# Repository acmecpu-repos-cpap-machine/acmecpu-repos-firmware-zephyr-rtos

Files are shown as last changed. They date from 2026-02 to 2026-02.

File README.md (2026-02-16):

## Zephyr RTOS Setup
To work with this project on **Zephyr RTOS**, follow these steps:

1. **Clone the repository:**
    ```bash
    git clone git@github.com:acmecpu-repos-cpap-machine/acmecpu-repos-firmware-zephyr-rtos.git
    cd acmecpu-repos-firmware-zephyr-rtos
    ```

2. **Install Zephyr and Dependencies:**
    Follow the [Zephyr Getting Started Guide](https://docs.zephyrproject.org/latest/getting_started/index.html) to install Zephyr RTOS and all required dependencies.

3. **Building the Firmware:**
    - Navigate to the desired application folder (e.g., `Blower_Driver_STSPIN32F0A`) and build the project:
    ```bash
    west build -b <your_board> .
    ```

4. **Flashing the Firmware:**
    Flash the firmware to the target hardware using your preferred flashing method (J-Link, ST-Link, etc.).

## CubeIDE Integration
For components that are developed using **STM32CubeIDE**, the IDE project files are located within relevant subfolders. To work with these projects, follow these steps:

1. Open STM32CubeIDE.
2. Import the relevant project (e.g., `Blower_Driver_STSPIN32F0A_E20x`).
3. Build and debug the project as per your requirements.

## Folder Details

### Blower_Driver_STSPIN32F0A
Contains the driver code for controlling the blower motor using **STSPIN32F0A** chip. The code is designed to work with **Zephyr RTOS** to control motor speed, direction, and provide fault monitoring.

### Blower_Driver_STSPIN32F0A_E20x
This folder contains the STM32CubeIDE project for the **STSPIN32F0A** driver, used for platform-specific configuration and debugging.

### altium_device_sheets
Contains the **Altium Designer** files for creating device schematics and PCB designs for Acme CPU hardware. These are used to design various control boards and sensor integration.

### bindings
This folder includes configuration files for various **GPIO** and **sensor** bindings that are required for integrating hardware components with Zephyr.

### bq25611d
Firmware integration for the **BQ25611D** battery management system. The code ensures proper charging, power monitoring, and management of lithium-ion batteries in embedded devices.

### buzzer_generic
This folder contains the driver for controlling a generic buzzer that is used for signaling in embedded applications. It is implemented using Zephyr's device driver framework.

### c201_esp32, c201_stm32g4
These folders contain the firmware for **C201 platform**, one based on **ESP32** and the other on **STM32G4**. These platforms are used for different hardware versions of the control board.

### c202_consolidate
Contains consolidated firmware for the **C202** platform, integrating all the different subsystems into one unified application.

### c20x_algo
This folder includes communication algorithms for the **C20X** series, used in embedded systems for efficient communication and data processing.

### control-board-c201
Contains hardware design files for the **C201 control board**. These are **Altium** files that include the circuit diagrams, PCB layout, and other related documents.

### lib_audio, lib_events, lib_file_oper, etc.
These libraries provide various functionalities such as audio signal processing, event handling, file operations, and more, all implemented for **Zephyr RTOS**. These are generic libraries that can be used across different embedded systems.

## Contributing
If you'd like to contribute to this repository, please follow these guidelines:
1. Fork the repository.
2. Create a new branch for your feature.
3. Make changes and commit them.
4. Submit a pull request to the main branch.
5. For more details please contact feel free to +1 617 401 8929

## License
This project is licensed under the MIT License - see the [LICENSE](LICENSE) file for details.

## Acknowledgements
Special thanks to **Zephyr RTOS** and **CubeIDE** for their continuous support in enabling embedded system development.

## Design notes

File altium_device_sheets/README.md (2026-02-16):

# altium_device_sheets
Repository to maintain Altium Device Sheets

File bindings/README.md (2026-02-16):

# bindings
Zephyr DTS bindings for devices not available on the main Zephyr repository

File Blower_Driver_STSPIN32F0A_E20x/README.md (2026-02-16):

# Blower_Driver_STSPIN32F0A_E20x
STSPIN32F0A based motor driver used in e20x series boards

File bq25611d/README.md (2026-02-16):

# bq25611d
Zephyr device driver for TI battery charger BQ25611D

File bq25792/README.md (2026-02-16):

# bq25792
Zephyr device driver for BQ25792 battery charger

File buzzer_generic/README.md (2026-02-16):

# buzzer_generic
Zephyr device driver for a generic buzzer

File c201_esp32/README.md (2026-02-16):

# C201 ESP32 Firmware

Repository to contain source files for the ESP32 based firmware for Control Board Model C201

## CLI commands to build, flash and monitor

- First export the environment by
`. $HOME/esp/esp-idf/export.sh`

- to build run
`idf.py build`

- to flash and monitor run (check your USB number by `ls -l /dev/ttyUSB*`)
`idf.py -p /dev/ttyUSB0 flash monitor`

- to erase the flash memory run
`idf.py -p /dev/ttyUSB0 erase_flash`

## Use Eclipse IDE to build, flash, monitor and debug

[GitHub - espressif/idf-eclipse-plugin: Eclipse plugin for ESP-IDF CMake based projects (4.x and above)](https://github.com/espressif/idf-eclipse-plugin#installing-idf-plugin-using-update-site-url)

[Using Debugger - ESP32 - — ESP-IDF Programming Guide v4.2 documentation](https://docs.espressif.com/projects/esp-idf/en/stable/esp32/api-guides/jtag-debugging/using-debugger.html#jtag-debugging-using-debugger-eclipse)

[JTAG Debugging - ESP32 - — ESP-IDF Programming Guide v4.2 documentation](https://docs.espressif.com/projects/esp-idf/en/stable/esp32/api-guides/jtag-debugging/index.html)

[esp-iot-solution/ESP-Prog_guide_en.md at master · espressif/esp-iot-solution](https://github.com/espressif/esp-iot-solution/blob/master/documents/evaluation_boards/ESP-Prog_guide_en.md)

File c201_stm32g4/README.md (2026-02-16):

# c201_stm32g4

Repository to contain source files for the STM32G473 based firmware for Control Board Model C201

# Build the project

Assuming the path to the project is $HOME/git/acme_cpu/c201_stm32g4/ and $HOME/zephyrproject/zephyr is the path to the Zephyr source code:

cd $HOME/zephyrproject/zephyr

source zephyr-env.sh (one time action to configure environment variables)

west build -p always -d $HOME/git/acme_cpu/c201_stm32g4/build $HOME/git/acme_cpu/c201_stm32g4/source -G"Eclipse CDT4 - Ninja"

or

west build -p auto -d $HOME/git/acme_cpu/c201_stm32g4/build $HOME/git/acme_cpu/c201_stm32g4/source -G"Eclipse CDT4 - Ninja"

if you do not necessarily need to build the project in a "pristine" build directory.

# Open the project in Eclipse IDE

Menu -> File -> Open Projects from File System...-> Select $HOME/git/acme_cpu/c201_stm32g4/ folder -> Open -> Select c201_stm32g4/build -> Finish

# Launch a GUI-based configuration tool (Kconfig)

cd $HOME/zephyrproject/zephyr

source zephyr-env.sh (one time action to configure environment variables)

west build -d $HOME/git/acme_cpu/c201_stm32g4/build -t guiconfig

# Flash a MCU with west

cd $HOME/zephyrproject/zephyr

source zephyr-env.sh (one time action to configure environment variables)

west flash -d $HOME/git/acme_cpu/c201_stm32g4/build --board-dir $HOME/git/acme_cpu/c201_stm32g4/source/boards\
	 -r openocd --config $HOME/git/acme_cpu/c201_stm32g4/source/boards/arm/stm32g473_acme_cpu_c201/support/openocd_st-link.cfg

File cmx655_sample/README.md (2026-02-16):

# cmx655_sample
Audio record and playback sample code using CMX655D audio codec

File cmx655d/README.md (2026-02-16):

# cmx655d
Zephyr device driver for CM655D Audio Codec

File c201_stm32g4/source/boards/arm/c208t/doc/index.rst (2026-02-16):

C208t board
################

Overview
********

Hardware
********

Supported Features
==================

System Clock
------------

Serial Port
-----------

Programming and Debugging
*************************

Flashing
========

Debugging
=========

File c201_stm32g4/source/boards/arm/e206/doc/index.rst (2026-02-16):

E206 board
################

Overview
********

Hardware
********

Supported Features
==================

System Clock
------------

Serial Port
-----------

Programming and Debugging
*************************

Flashing
========

Debugging
=========

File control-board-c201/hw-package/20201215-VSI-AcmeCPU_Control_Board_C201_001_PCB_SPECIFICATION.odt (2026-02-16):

Specification for PCB: Control_Board_C201.PcbDoc

The 6-layer PCB is intended for manual and automatic soldering of SMT and THT parts on the top and bottom sides .

General requirements

IPC-A-600/6010 class 2

Laminate

Laminate: IPC 4101/21 with minimum Tg=130°C

Flammability: V0 according to UL94

CTI index 3: 175 < CTI ≤ 400 or better

CTE: Pre-Tg. 60ppm/°C Post-Tg. 300ppm/°C

Copper plating

Hole plating: min. 20μm. and min. avg. 25μm according to IPC-6012 class 3

Dimensions and Marking

PCB Size (X,Y): 100x70 mm

Tolerances on outline dimensions: +/- 0.2mm

Layer stackup

The PCB stack is in the picture below. The total thickness of the PCB is 1,22 mm ±10%.

Controlled impedance traces

Controlled impedance traces are as follows.

Layer | Impedance Structure | Trace width, mm | Diff line space, mm | 1 ref. plane | 2 ref. plane | Target Impedance, Ohm*
1 | Edge Coupled Coated Microstrip | 0.152 | 0.152 | 2 | - | 90 diff
1 | Single Ended | 0.152 | - | 2 | - | 50
2
3
4
5
6

*Tolerance on all impedances is ±10%.

Solder mask

Liquid film or electrostatic spray coating on top and bottom sides .

According to: IPC-SM-840E, Class T

Minimum thickness: 8μm

Maximum thickness: 30μm

Legend:

Silkscreen Colour: White on top and bottom layers.

Plugged via holes:

Via holes covered by solder mask on both sides must be plugged.

Via holes with solder mask opening on one side and covered by solder mask on the other side, must be plugged from the same side they are covered by solder mask – solder mask opening on the other side must remain.

Surface finish

ENIG – Au 0.05 μm / Ni 3.0 μm;

Solderability accordingly to IPC J-STD-003, test C1 PTH, SMD test F1 set A

Gerber data (.\Manufacturing\Gerber Files)

Filename | Contents
20201215-VSI-AcmeCPU_Control_Board_C201_001_PCB_SPECIFICATION.pdf | This file
20201215-VSI-Acme_CPU_Control_Board_C201_001_Gerber.GTL | Layer 1, 1-SIG-Top
20201215-VSI-Acme_CPU_Control_Board_C201_001_Gerber.GP1 | Layer 2, 2-GND
20201215-VSI-Acme_CPU_Control_Board_C201_001_Gerber.GP2 | Layer 3, 3-PWR
20201215-VSI-Acme_CPU_Control_Board_C201_001_Gerber.G1 | Layer 4, 4-SIG-HOR
20201215-VSI-Acme_CPU_Control_Board_C201_001_Gerber.G2 | Layer 5, 5-SIG-VERT
20201215-VSI-Acme_CPU_Control_Board_C201_001_Gerber.GBL | Layer 6, 6-GND-BOT
20201215-VSI-Acme_CPU_Control_Board_C201_001_Gerber.GTO | Top Overlay (Top Silk)
20201215-VSI-Acme_CPU_Control_Board_C201_001_Gerber.GTS | Top Solder (Solder Mask)
20201215-VSI-Acme_CPU_Control_Board_C201_001_Gerber.GBS | Bottom Solder (Solder Mask)
20201215-VSI-Acme_CPU_Control_Board_C201_001_Gerber.GBO | Bottom Overlay
20201215-VSI-Acme_CPU_Control_Board_C201_001_Gerber.GM12 | Board Outline
20201215-VSI-Acme_CPU_Control_Board_C201_001_Gerber.GD1 | Drill Drawing
20201215-VSI-Acme_CPU_Control_Board_C201_001_Gerber.GG1 | Drill Guide
20201215-VSI-Acme_CPU_Control_Board_C201_001_Gerber.GM14 | Top Assembly
20201215-VSI-Acme_CPU_Control_Board_C201_001_Gerber.GM19 | Bottom Assembly

Stencils (.\Manufacturing\Stencil Files)

Filename | Contents
20201215-VSI-Acme_CPU_Control_Board_C201_001_Stencil.GTP | Top Paste
20201215-VSI-Acme_CPU_Control_Board_C201_001_Stencil.GBP | Bottom Paste

Drill and milling data (.\Manufacturing\Gerber Files)

Filename | Contents
20201215-VSI-Acme_CPU_Control_Board_C201_001_NC_Drill-RoundHoles-NonPlated.TXT | NCDrill Non-plated Round Holes File
20201215-VSI-Acme_CPU_Control_Board_C201_001_NC_Drill-SlotHoles-Plated.TXT | NCDrill Plated Slot Holes File
20201215-VSI-30041113_Acme_CPU_Control_Board_C201_001_NC_Drill-RoundHoles-Plated.TXT | NCDrill Plated Round Holes File

Text Reports

Filename | Contents
20201215-VSI-Acme_CPU_Control_Board_C201_001_Gerber.REP | Gerber Generation report
20201215-VSI-Acme_CPU_Control_Board_C201_001_Gerber.EXTREP | Gerber File Extension Report
20201215-VSI-Acme_CPU_Control_Board_C201_001_NC_Drill.DRR | NCDrill File Report
20201215-VSI-Acme_CPU_Control_Board_C201_001_Stencil.REP | Stencil Generation report
20201215-VSI-Acme_CPU_Control_Board_C201_001_Stencil.EXTREP | Gerber File Extension Report

Schematic (.\Design\Schematic - pdf)

Assembly Drawings (.\Assembly\PCB Layout - pdf)

20201215-VSI-Acme_CPU_Control_Board_C201_001_PCB.PDF

20201215-VSI-Acme_CPU_Control_Board_C201_001_DWG.PDF

Pick and Place (.\Assembly\Pick_n_Place)

BG95-M3_Global_TFT_SCREEN\20201215-VSI-Acme_CPU_Control_Board_C201_001_Pick_and_Place.txt

BOM (.\Assembly\BOM - Excel)

BG95-M3_Global_TFT_SCREEN\20201215-VSI-Acme_CPU_Control_Board_C201_001_BG95-M3_Global_TFT_SCREEN_DFM_BOM.xls

Additional info

Mechanical Files (.\Assembly\Mechanical)

No Variations\20201215-VSI-Acme_CPU_Control_Board_C201_001_DXF_Model.DXF

BG95-M3_Global_TFT_SCREEN\20201215-VSI-Acme_CPU_Control_Board_C201_001_BG95-M3_Global_TFT_SCREEN_3D.step

General

Extended gerber / excellon drill.

Layout

Filename: Altium 17.1: Control_Board_Model_C201_FFC_Sens_Conn.PcbDoc

Fiducials

TOP FID1: 2.54mm; 62.865mm

TOP FID2: 2.54mm; 7.62mm

TOP FID3: 93.98mm; 6.35mm

BOT FID1: 2.54mm; 62.865mm

BOT FID2: 2.54mm; 7.62mm

BOT FID3: 93.98mm; 6.35mm

Contacts

If there are any questions regarding the layout please contact:

HW Developer

Volodymyr Sirous

Email: volodymyr@acmecpu.com

Project Manager

Pankaj Gupta

Email: pg@acmecpu.com

Homepage: www.acmecpu.com

Acme CPU PCB Specification Page 2/4 Date: 20201215 Acme_CPU_Control_Board_C201_001 Responsible: VSI

Acme CPU 30 N Gould St suite 4000 ● Sheridan WY 82801 ● USA (http://www.ektos.net/)● (http://www.ektos.net/)info@acmecpu.com (http://www.ektos.net/)● (http://www.ektos.net/)http://www.acmecpu.com

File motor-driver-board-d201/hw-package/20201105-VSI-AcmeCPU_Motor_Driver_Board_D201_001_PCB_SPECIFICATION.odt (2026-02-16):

Specification for PCB: Motor_Driver_D201.PcbDoc

The 4-layer PCB is intended for manual and automatic soldering of SMT and THT parts on the top side.

General requirements

IPC-A-600/6010 class 2

Laminate

Laminate: IPC 4101/124 with minimum Tg=150°C

Flammability: V0 according to UL94

CTI index 3: 175 < CTI ≤ 400 or better

CTE: Pre-Tg. 60ppm/°C Post-Tg. 300ppm/°C

Copper plating

Hole plating: min. 20μm. and min. avg. 25μm according to IPC-6012 class 3

Dimensions and Marking

PCB Size (X,Y): 20x30 mm

Tolerances on outline dimensions: +/- 0.2mm

Layer stackup

The PCB stack is in the picture below. The total thickness of the PCB is 0,98 mm ±10%.

Controlled impedance traces

There is no need to control impedance of traces on the PCB.

Layer | Impedance Structure | Trace width, mm | Diff line space, mm | 1 ref. plane | 2 ref. plane | Target Impedance, Ohm*
1
2
3
4
5
6

*Tolerance on all impedances is ±10%.

Solder mask

Liquid film or electrostatic spray coating on top and bottom sides .

According to: IPC-SM-840E, Class T

Minimum thickness: 8μm

Maximum thickness: 30μm

Legend:

Silkscreen Colour: White on top and bottom layers.

Plugged via holes:

Via holes covered by solder mask on both sides must be plugged.

Via holes with solder mask opening on one side and covered by solder mask on the other side, must be plugged from the same side they are covered by solder mask – solder mask opening on the other side must remain.

Surface finish

ENIG – Au 0.05 μm / Ni 3.0 μm;

Solderability accordingly to IPC J-STD-003, test C1 PTH, SMD test F1 set A

Gerber data (.\Manufacturing\Gerber Files)

Filename | Contents
20201105-VSI-AcmeCPU_Motor_Driver_Board_D201_001_PCB_SPECIFICATION.pdf | This file
20201105-VSI-Acme_CPU_Motor_Driver_D201_001_Gerber.GTL | Layer 1, 1-SIG-Top
20201105-VSI-Acme_CPU_Motor_Driver_D201_001_Gerber.GP1 | Layer 2, 2-GND
20201105-VSI-Acme_CPU_Motor_Driver_D201_001_Gerber.GP2 | Layer 3, 3-GND-PWR
20201105-VSI-Acme_CPU_Motor_Driver_D201_001_Gerber.GBL | Layer 4, 4-SIG-BOT
20201105-VSI-Acme_CPU_Motor_Driver_D201_001_Gerber.GTO | Top Overlay (Top Silk)
20201105-VSI-Acme_CPU_Motor_Driver_D201_001_Gerber.GTS | Top Solder (Solder Mask)
20201105-VSI-Acme_CPU_Motor_Driver_D201_001_Gerber.GBS | Bottom Solder (Solder Mask)
20201105-VSI-Acme_CPU_Motor_Driver_D201_001_Gerber.GBO | Bottom Overlay
20201105-VSI-Acme_CPU_Motor_Driver_D201_001_Gerber.GM12 | Board Outline
20201105-VSI-Acme_CPU_Motor_Driver_D201_001_Gerber.GD1 | Drill Drawing
20201105-VSI-Acme_CPU_Motor_Driver_D201_001_Gerber.GG1 | Drill Guide
20201105-VSI-Acme_CPU_Motor_Driver_D201_001_Gerber.GM14 | Top Assembly

Stencils (.\Manufacturing\Stencil Files)

Filename | Contents
20201105-VSI-Acme_CPU_Motor_Driver_D201_001_Stencil.GTP | Top Paste

Drill and milling data (.\Manufacturing\Gerber Files)

Filename | Contents
20201105-VSI-30041113_Acme_CPU_Motor_Driver_D201_001_NC_Drill-Plated.TXT | NCDrill Plated Holes File

Text Reports

Filename | Contents
20201105-VSI-Acme_CPU_Motor_Driver_D201_001_Gerber.REP | Gerber Generation report
20201105-VSI-Acme_CPU_Motor_Driver_D201_001_Gerber.EXTREP | Gerber File Extension Report
20201105-VSI-Acme_CPU_Motor_Driver_D201_001_NC_Drill.DRR | NCDrill File Report
20201105-VSI-Acme_CPU_Motor_Driver_D201_001_Stencil.REP | Stencil Generation report
20201105-VSI-Acme_CPU_Motor_Driver_D201_001_Stencil.EXTREP | Gerber File Extension Report

Schematic (.\Design\Schematic - pdf)

20201105-VSI-Acme_CPU_Motor_Driver_D201_001_No Variations.PDF

Assembly Drawings (.\Assembly\PCB Layout - pdf)

20201105-VSI-Acme_CPU_Motor_Driver_D201_001_PCB.PDF

Pick and Place (.\Assembly\Pick_n_Place)

20201105-VSI-Acme_CPU_Motor_Driver_D201_001_Pick_and_Place.txt

BOM (.\Assembly\BOM - Excel)

20201105-VSI-Acme_CPU_Motor_Driver_D201_001_No_Variatoins_DFM_BOM.xls

Additional info

Mechanical Files (.\Assembly\Mechanical)

20201105-VSI-Acme_CPU_Motor_Driver_D201_001_Plain_AutoCAD.DXF

20201105-VSI-Acme_CPU_Motor_Driver_D201_001_3D_STEP.step

General

Extended gerber / excellon drill.

Layout

Filename: Altium 17.1: Motor_Driver_D201.PcbDoc

Fiducials

TOP FID1: 7.50mm; 18.00mm

TOP FID2: 20.50mm; 18.00mm

TOP FID3: 27.94mm; 7.62mm

Contacts

If there are any questions regarding the layout please contact:

HW Developer

Volodymyr Sirous

Email: volodymyr@acmecpu.com

Project Manager

Pankaj Gupta

Email: pg@acmecpu.com

Homepage: www.acmecpu.com

Acme CPU PCB Specification Page 2/4 Date: 20201105 Acme_CPU_Motor_Driver_D201_001 Responsible: VSI

Acme CPU 30 N Gould St suite 4000 ● Sheridan WY 82801 ● USA (http://www.ektos.net/)● (http://www.ektos.net/)info@acmecpu.com (http://www.ektos.net/)● (http://www.ektos.net/)http://www.acmecpu.com

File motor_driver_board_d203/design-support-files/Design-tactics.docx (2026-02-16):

1. Separated Microcontroller Portion from High Power circuitry.

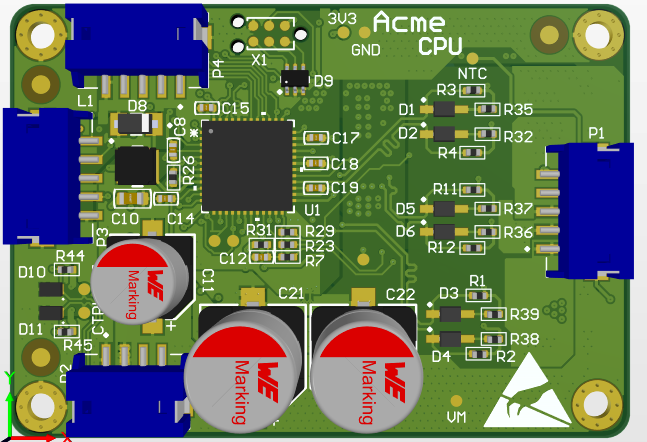
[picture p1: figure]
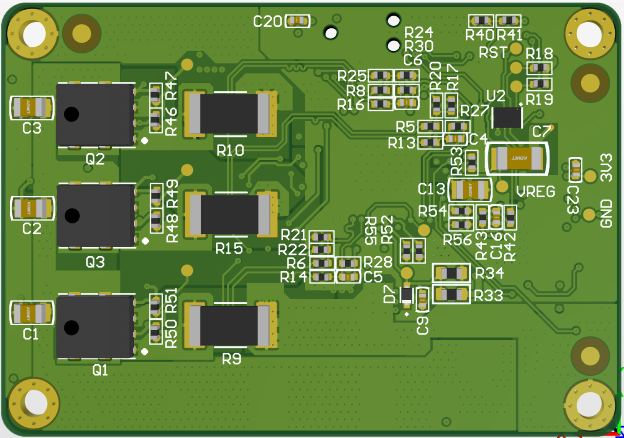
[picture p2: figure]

2. Placed the Input Connector as close as possible to compensate with the shorter high power path to the H-Bridge Section.
3. Minimized the AC loop Area. Used Multilayer return topology to return the Current. Since the Internal Plane layers does not have air proximity, multilayer return path is useful to reduce the resistance (Lowering the heat dissipation due to high current flow).

POWER SOURCE LAYERs

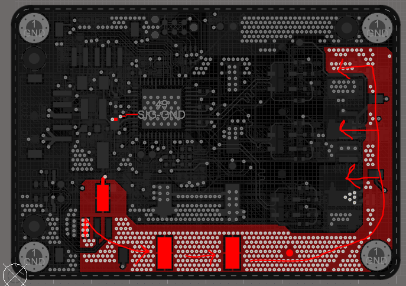
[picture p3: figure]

The Motor Power flowing through the 1st Layer (TOP)

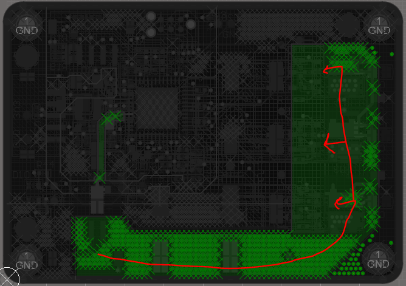
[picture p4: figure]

The Motor Power flowing through the 2md Layer

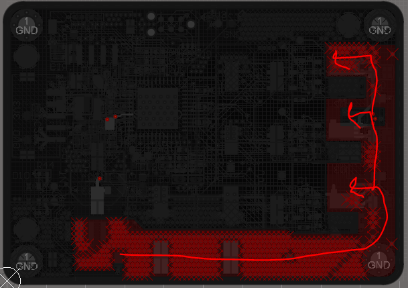
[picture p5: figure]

The Motor Power flowing through the 3rd Layer

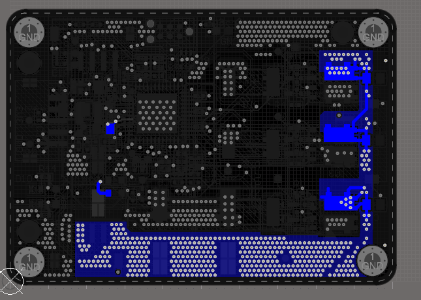
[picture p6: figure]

The Motor Power flowing through the 4^t^h Layer (BOTTOM)

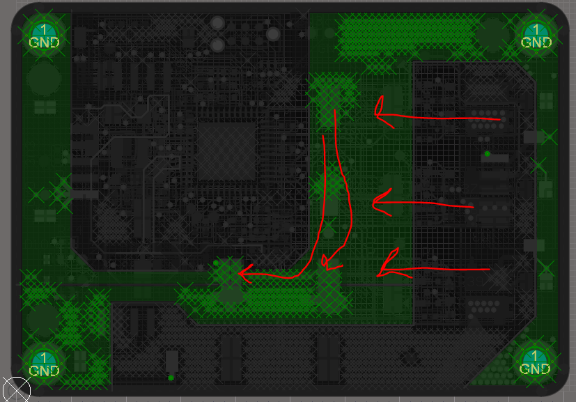
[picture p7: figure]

GROUND REURN LAYERs

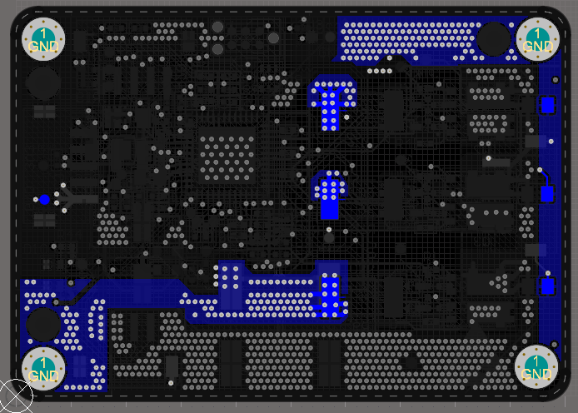
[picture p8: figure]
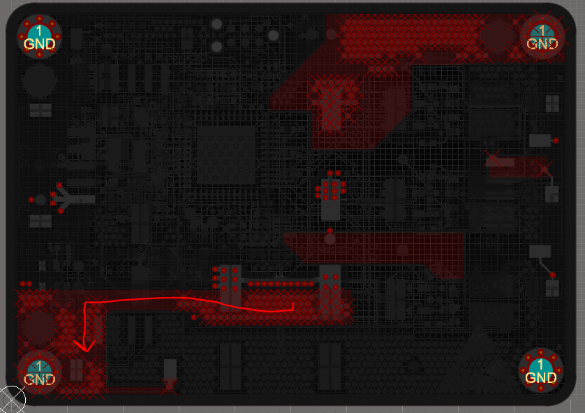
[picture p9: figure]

The Motor Current Returning to the Input Filter Caps.

The current is coming to the Input Power port through the
Capacitor using the 3rd Layer.

The current is also coming to the Input Power port through
the Capacitor using the 4th Layer.

4. Separation of Ground Paths and isolation are done to reduce unwanted noise injunction. Returned to the Bulk Capacitor. As two Bulk capacitors are used to reduce increase the capacitance, decreasing the height and lowering the ESR value, the separation of ground on start pattern is done.

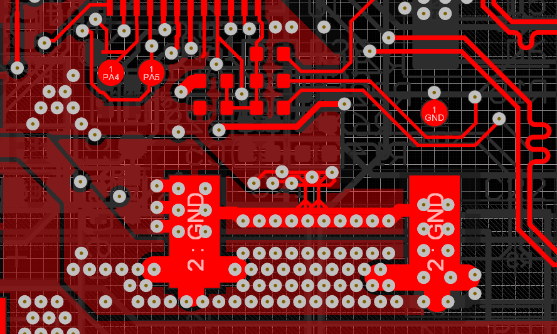
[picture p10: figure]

Two net ties are used to separate the MCU Ground from the Power Ground and joined across in between of the Bulk Caps Pads.

Different Ground Signal Return Paths (Primary Layer shown only)–

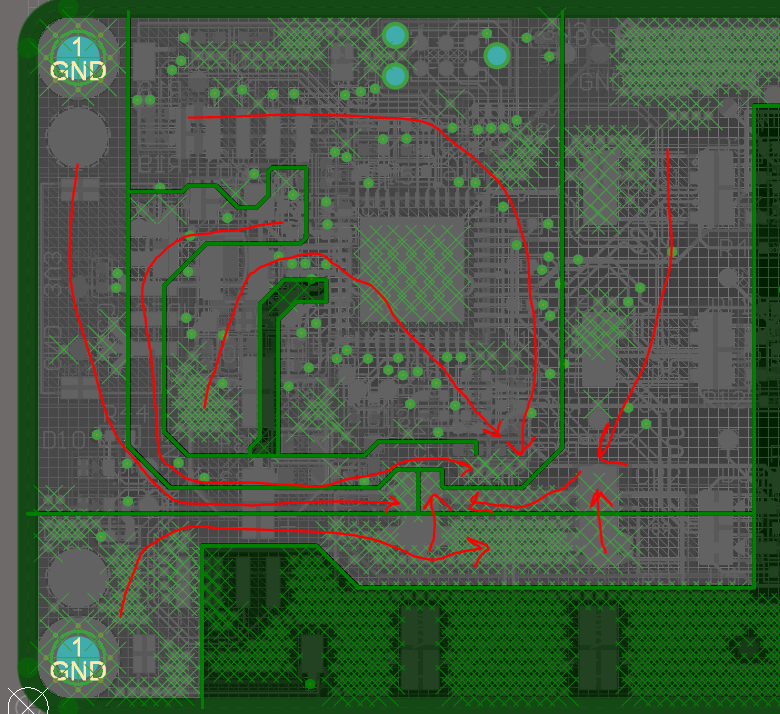
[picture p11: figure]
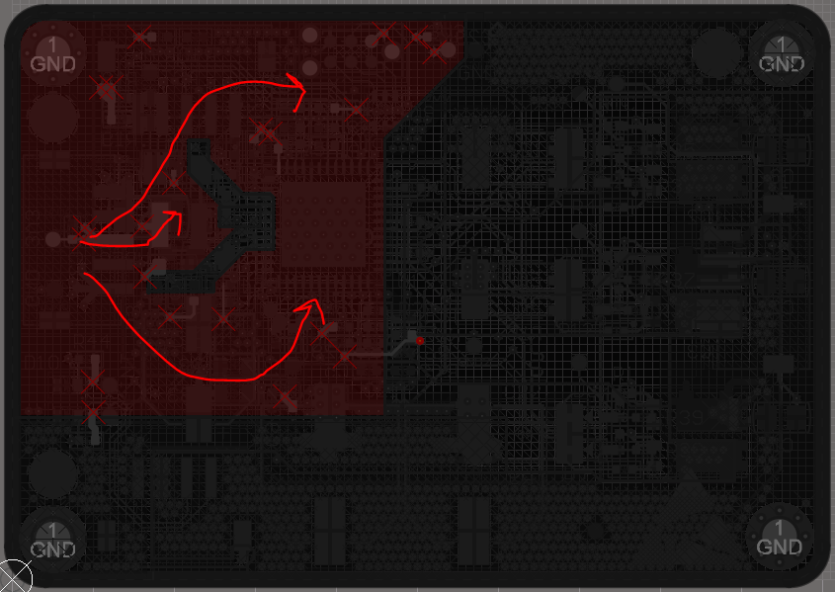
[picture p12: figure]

5. Separate MCU Power Path Created for 3.3V line which comes from external regulator sources out of the board. Close proximity of the Filter capacitors are placed.

The return path goes like this –

MCU Ground & sense circuit ground-> Bulk Capacitor -> Input Connector.

[Please note: The ground for the Motor Power and 3.3V external Ground are connected to the same source coming from external Power circuit]

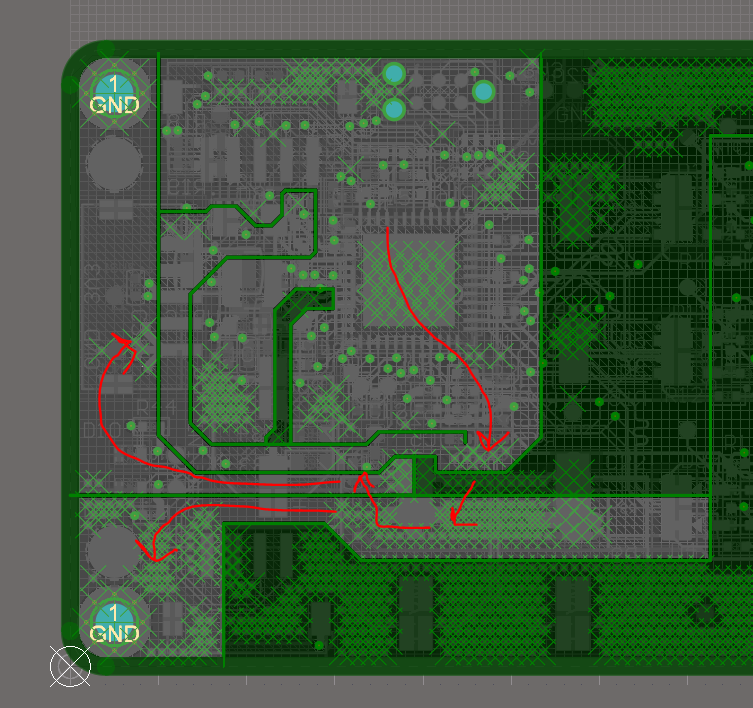
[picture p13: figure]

6. Array of Vias and Multi-layer Planes are used to carry current.
7. Gate resistor and circuitry are placed into close proximity.

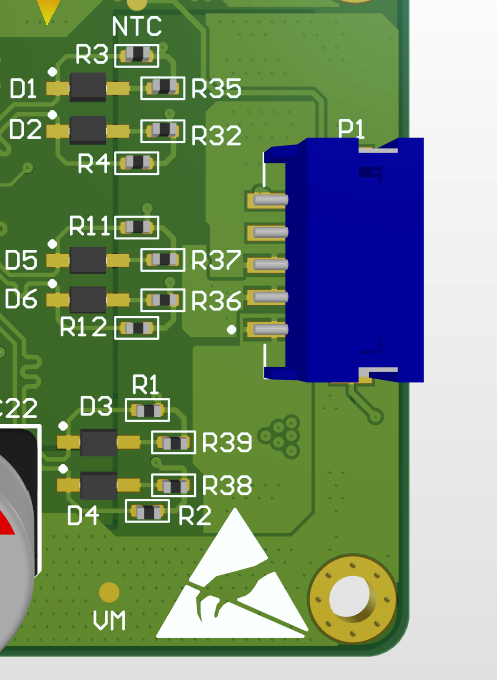
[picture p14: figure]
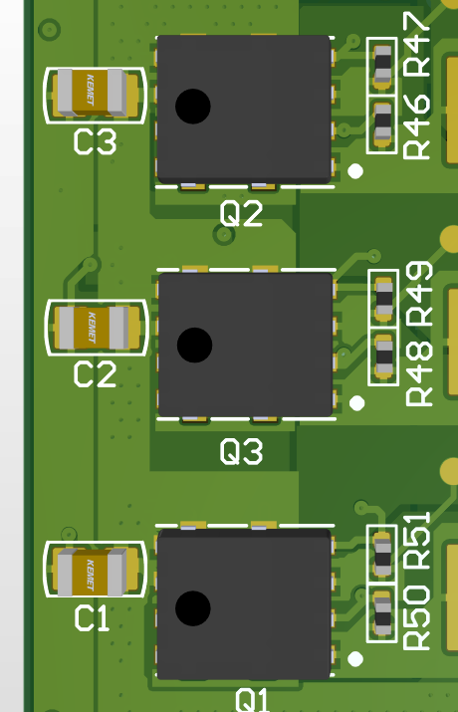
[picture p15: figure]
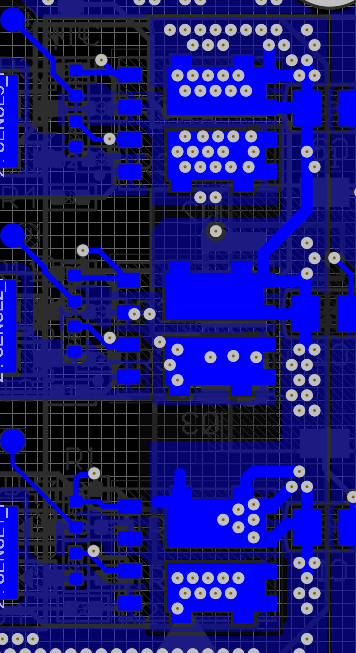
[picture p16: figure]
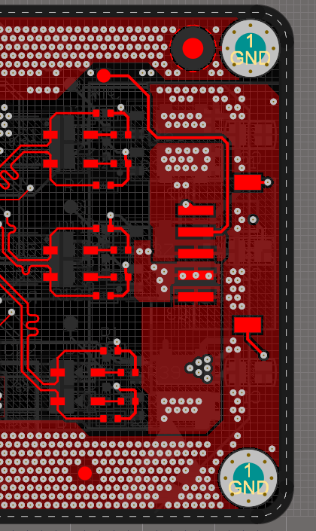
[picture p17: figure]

8. Kelvin sensing used and differential length tuning is done.

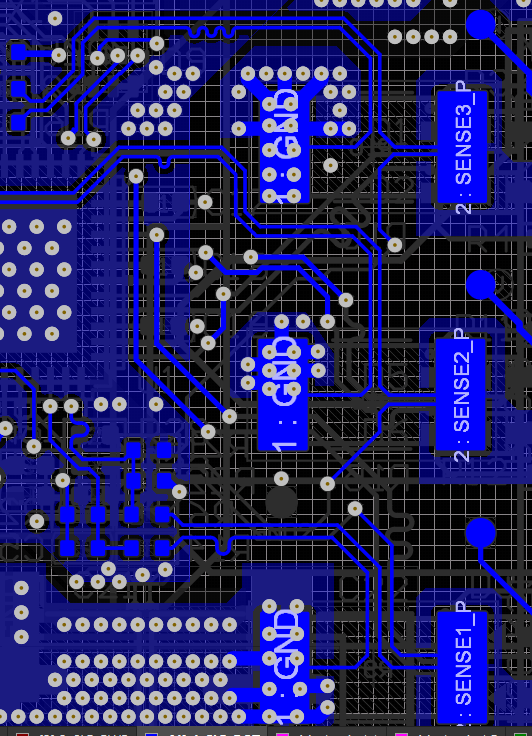
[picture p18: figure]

Op-Amp differential inputs are also tuned –

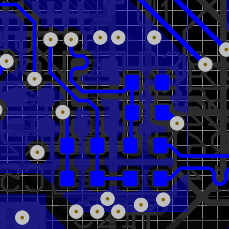
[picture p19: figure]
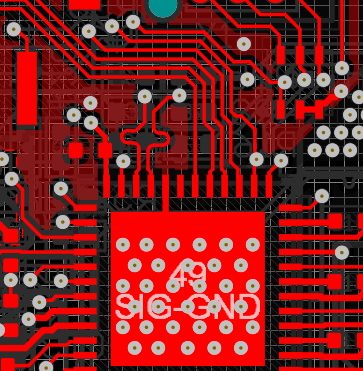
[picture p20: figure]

9. Gate driver of Three phases – Low Side and High Sides are connected parallel, differential pairs used where length tuning is done.

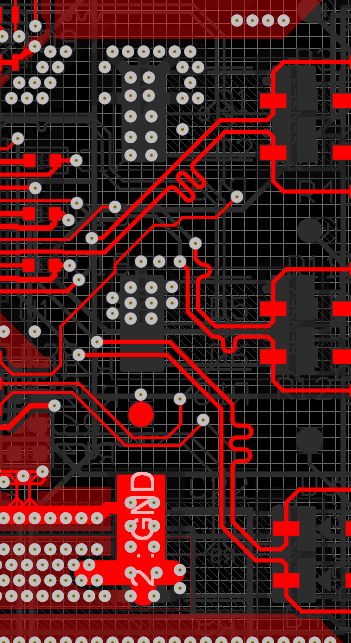
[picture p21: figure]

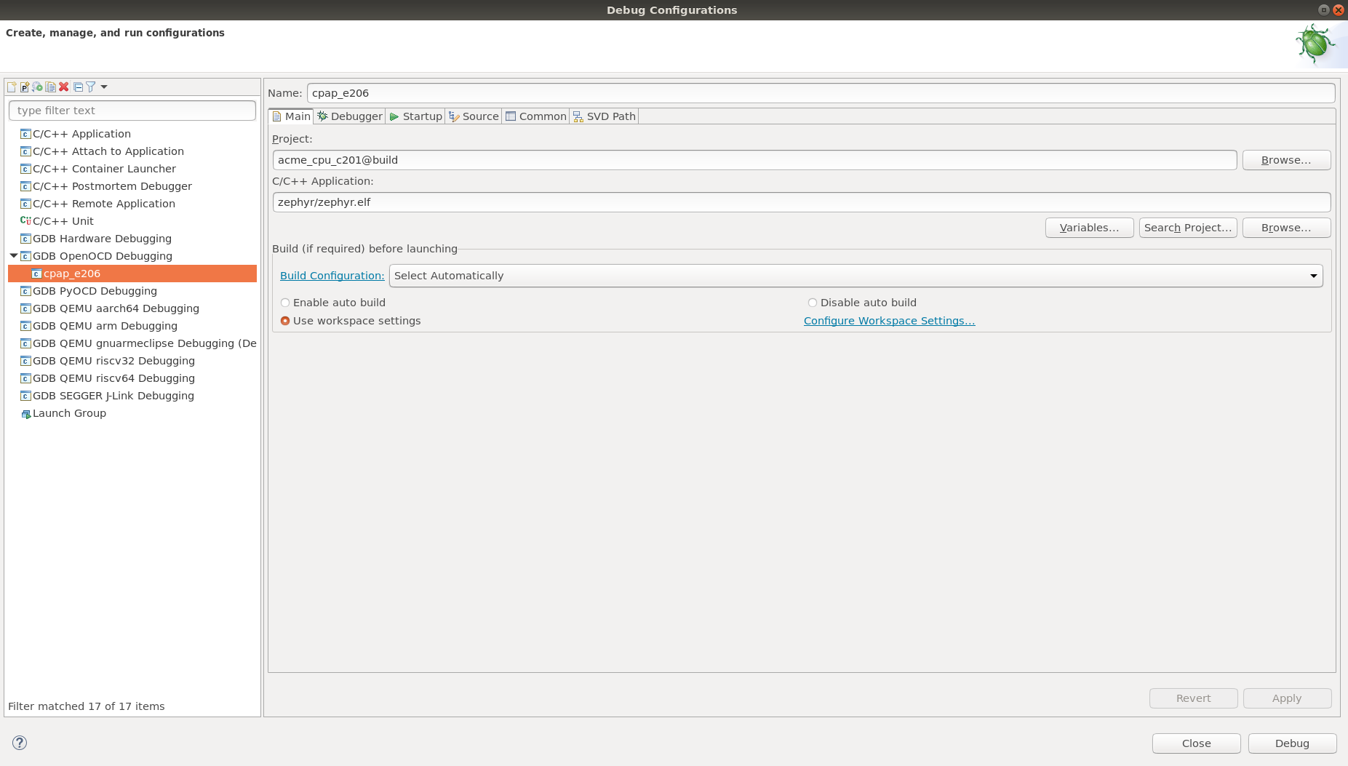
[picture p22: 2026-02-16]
firmware_general/openocd/openocd_eclipse_main.png

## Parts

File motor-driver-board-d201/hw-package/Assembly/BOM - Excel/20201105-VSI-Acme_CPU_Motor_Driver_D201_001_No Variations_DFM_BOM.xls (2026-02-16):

Designator | Quantity | Manufacturer | Manufacturer Part Number | Comment | Description | Footprint | Mount | Layer | Supplier 1 | Supplier Part Number 1
C1, C4, C9, C10 | 4.0 | TDK | CGA2B3X7R1H104K050BB | CAP CER 0.1UF 50V X7R 0402, CAP CER 0.1UF 50V X7R 0402, CGA2B3X7R1H104K050BB, CGA2B3X7R1H104K050BB | 0.1µF ±10% 50V Ceramic Capacitor X7R 0402 (1005 Metric) | C0402 | Surface Mount | Top | Digi-Key | 445-6899-1-ND
C2, C3, C8 | 3.0 | Yageo | CC0402KRX5R5BB105 | CAP CER 1UF 6.3V X5R 0402 | 1µF ±10% 6.3V Ceramic Capacitor X5R 0402 (1005 Metric) | C0402 | Surface Mount | Top | Digi-Key | 311-1438-1-ND
C5 | 1.0 | Yageo | CC0805MKX5R8BB226 | CAP CER 22UF 25V X5R 0805 | 22µF ±20% 25V Ceramic Capacitor X5R 0805 (2012 Metric) | C0805 | Surface Mount | Top | Digi-Key | 311-1903-1-ND
C6 | 1.0 | Murata | GRM21BR71A106KA73L | CAP CER 10uF X7R 10% 0805 | Capacitor,10uF,10V,X7R,10%,0805,Murata | C0805 | Surface Mount | Top | Digi-Key | 490-10516-1-ND
C7 | 1.0 | Wurth Elektronik | 865080443009 | CAP ALUM 68 UF 20% 25 V SMD | WCAP-ASLI Aluminum Electrolytic Capacitor, V-Chip, SMT, D6.3xH5.5mm, 68uF, 25V | WCAP-ASLI_6.3x5.5 | Surface Mount | Top | Digi-Key | 732-8437-1-ND
D1 | 1.0 | ON Semiconductor | 1SMF5920BT1G | Zener Diode 6.2V 2.5W ±5% Surface Mount SOD-123FL | Zener Diode 6.2V 2.5W ±5% Surface Mount SOD-123FL | SOD-123FL | Surface Mount | Top | Digi-Key | 1SMF5920BT1GOSCT-ND
D2 | 1.0 | STMicroelectronics | ESDA7P120-1U1M | ESDA7P120-1U1M | 11.5V Clamp 120A (8/20µs) Ipp Tvs Diode Surface Mount 1610 | ST_QFN_1610 | Surface Mount | Top | Digi-Key | 497-17159-1-ND
P17, P402 | 2.0 | JST | S5B-ZR(LF)(SN) | BLDC Motor, I2C | Connector Header Through Hole, Right Angle 5 position 0.059" (1.50mm) | CONN_S5B-ZR(LF)(SN) | Through Hole | Top | Digi-Key | 455-1672-ND
P401 | 1.0 | JST | S4B-ZR(LF)(SN) | PWR_IN | Connector Header Through Hole, Right Angle 4 position 0.059" (1.50mm) | CONN_S4B-ZR(LF)(SN) | Through Hole | Top | Arrow | S4B-ZR(LF)(SN)
R3 | 1.0 | Yageo | RC0402FR-074K75P | RES SMD 4.75K OHM 1% 1/16W 0402 | 4.75 kOhms ±1% 0.063W, 1/16W Chip Resistor 0402 (1005 Metric) Moisture Resistant Thick Film | R0402 | Surface Mount | Top | Digi-Key | YAG1271CT-ND
R4 | 1.0 | Yageo | RC1206JR-0739RL | RES SMD 39 OHM 1% 1/4W 1206 | 39 Ohms ±5% 0.25W, 1/4W Chip Resistor 1206 (3216 Metric) Moisture Resistant Thick Film | R1206 | Surface Mount | Top | Digi-Key | 311-39ERCT-ND
U1 | 1.0 | Texas Instruments | DRV10975ZRHFR | DRV10975ZRHFR | Multiphase Motor Driver Power MOSFET Analog, I²C, PWM 24-VQFN (5x4) | RHF24_2P65X3P65 | Surface Mount | Top | Digi-Key | 296-50214-1-ND
U2 | 1.0 | Texas Instruments | TPD3F303DPVR | TPD3F303DPVR | RC (Pi) EMI Filter 2nd Order Low Pass 3 Channel R = 47Ohms, 100Ohms, C = 20pF 8-UFDFN Exposed Pad | DPV8_1P7X0P4 | Surface Mount | Top | Digi-Key | 296-28299-1-ND
U3 | 1.0 | Texas Instruments | TXS0102DQMR | TXS0102DQMR | 2-Bit Bidirectional Voltage-Level Translator for Open-Drain Application | DQM8 | Surface Mount | Top | Digi-Key | 296-28435-1-ND

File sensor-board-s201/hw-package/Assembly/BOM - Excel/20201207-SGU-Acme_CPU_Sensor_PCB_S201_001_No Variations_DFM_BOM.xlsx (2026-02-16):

Designator | Quantity | Manufacturer | Manufacturer Part Number | Comment | Description | Footprint | Mount | Layer | Supplier 1 | Supplier Part Number 1
C1 | 1 | TDK | CGA2B3X7R1H104K050BB | CAP CER 0.1UF 50V X7R 0402 | 0.1µF ±10% 50V Ceramic Capacitor X7R 0402 (1005 Metric) | C0402 | Surface Mount | Top | Digi-Key | 445-6899-1-ND
C2 | 1 | Yageo | CC0402KRX5R5BB105 | CAP CER 1UF 6.3V X5R 0402 | 1µF ±10% 6.3V Ceramic Capacitor X5R 0402 (1005 Metric) | C0402 | Surface Mount | Top | Digi-Key | 311-1438-1-ND
C3, C4, C5, C6 | 4 | YAGEO | CC0402KRX7R7BB104 | CAP CER 0.1UF 16V X7R 0402 | 0.1µF ±10% 16V Ceramic Capacitor X7R 0402 (1005 Metric) | C0402 | Surface Mount | Bottom | Digi-Key | 311-1338-1-ND
FB1, FB2 | 2 | Murata | BLM15AX102SN1D | FERRITE BEAD 1 KOHM 0402 1LN | 1 kOhms @ 100MHz 1 Ferrite Bead 0402 (1005 Metric) 350mA 490mOhm | L0402 |  | Bottom | Digi-Key | 490-5442-1-ND
R1 | 1 | Yageo | RC0402JR-070RL | RES SMD 0 OHM JUMPER 1/16W 0402 | 0 Ohms Jumper 0.063W, 1/16W Chip Resistor 0402 (1005 Metric) Moisture Resistant Thick Film | R0402 |  | Top | Digi-Key | 311-0.0JRCT-ND
U1 | 1 | Texas Instruments | TPD3F303DPVR | TPD3F303DPVR | RC (Pi) EMI Filter 2nd Order Low Pass 3 Channel R = 47Ohms, 100Ohms, C = 20pF 8-UFDFN Exposed Pad | DPV8_1P7X0P4 |  | Top | Digi-Key | 296-28299-1-ND
U2, U3 | 2 | Bosch Sensortec | BMP388 | BMP388 | Pressure Sensor 4.35PSI ~ 18.13PSI (30kPa ~ 125kPa) Absolute 10-WFLGA | QFN_BMP388_BOS | Surface Mount | Top | Digi-Key | 828-1079-1-ND

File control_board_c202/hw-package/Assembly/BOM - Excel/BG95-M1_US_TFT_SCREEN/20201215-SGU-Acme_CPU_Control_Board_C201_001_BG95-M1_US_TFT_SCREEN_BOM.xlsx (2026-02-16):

Designator | Manufacturer Part Number | Quantity | Comment | Description
B1 | CPH3225A | 1 | CAP 11MF 3.3V SURFACE MNT | 11mF (EDLC) Supercapacitor 3.3V 1210 (3225 Metric)
BTN1 | USLPT2819DT2TR | 1 | RESET | Tactile Switch SPST-NO Top Actuated Surface Mount
BTN2 | USLPT2819DT2TR | 1 | BOOT | Tactile Switch SPST-NO Top Actuated Surface Mount
C1 | CC0603KRX5R7BB105 | 1 | CAP CER 1UF 16V X5R 0603 | 1µF ±10% 16V Ceramic Capacitor X5R 0603 (1608 Metric)
C2 | CGA2B3X7R1H473K050BB | 1 | CAP CER 0.047UF 50V X7R 0402 | 0.047µF ±10% 50V Ceramic Capacitor X7R 0402 (1005 Metric)
C3 | CC0603KRX5R6BB475 | 1 | CAP CER 4.7UF 10V X5R 0603 | 4.7µF ±10% 10V Ceramic Capacitor X5R 0603 (1608 Metric)
C4 | CC1206KKX7R8BB106 | 1 | CAP CER 10UF 25V X7R 1206 | 10µF ±10% 25V Ceramic Capacitor X7R 1206 (3216 Metric)
C5 | GRM21BR71A106KA73L | 1 | CAP CER 10uF X7R 10% 0805 | Capacitor,10uF,10V,X7R,10%,0805,Murata
C6 | GRM21BR71A106KA73L | 1 | CAP CER 10uF X7R 10% 0805 | Capacitor,10uF,10V,X7R,10%,0805,Murata
C7 | GRM21BR71A106KA73L | 1 | CAP CER 10uF X7R 10% 0805 | Capacitor,10uF,10V,X7R,10%,0805,Murata
C8 | GRM21BR71A106KA73L | 1 | CAP CER 10uF X7R 10% 0805 | Capacitor,10uF,10V,X7R,10%,0805,Murata
C9 | CGA2B3X7R1H104K050BB | 1 | CAP CER 0.1UF 50V X7R 0402 | 0.1µF ±10% 50V Ceramic Capacitor X7R 0402 (1005 Metric)
C10 | CGA2B3X7R1H104K050BB | 1 | CAP CER 0.1UF 50V X7R 0402 | 0.1µF ±10% 50V Ceramic Capacitor X7R 0402 (1005 Metric)
C11 | AC0402CRNPO9BN5R6 | 1 | CAP CER 5.6PF 50V NPO 0402 | 5.6pF ±0.25pF 50V Ceramic Capacitor C0G, NP0 0402 (1005 Metric)
C12 | AC0402CRNPO9BN5R6 | 1 | CAP CER 5.6PF 50V NPO 0402 | 5.6pF ±0.25pF 50V Ceramic Capacitor C0G, NP0 0402 (1005 Metric)
C13 | 865080443009 | 1 | CAP ALUM 68 UF 20% 25 V SMD | 68µF 25V Aluminum Electrolytic Capacitors Radial, Can - SMD 2000 Hrs @ 105°C
C14 | 865080443009 | 1 | CAP ALUM 68 UF 20% 25 V SMD | 68µF 25V Aluminum Electrolytic Capacitors Radial, Can - SMD 2000 Hrs @ 105°C
C15 | 865080443009 | 1 | CAP ALUM 68 UF 20% 25 V SMD | 68µF 25V Aluminum Electrolytic Capacitors Radial, Can - SMD 2000 Hrs @ 105°C
C16 | CC0402KRX5R5BB105 | 1 | CAP CER 1UF 6.3V X5R 0402 | 1µF ±10% 6.3V Ceramic Capacitor X5R 0402 (1005 Metric)
C17 | CGA2B3X7R1H104K050BB | 1 | CAP CER 0.1UF 50V X7R 0402 | 0.1µF ±10% 50V Ceramic Capacitor X7R 0402 (1005 Metric)
C18 | CGA2B3X7R1H104K050BB | 1 | CAP CER 0.1UF 50V X7R 0402 | 0.1µF ±10% 50V Ceramic Capacitor X7R 0402 (1005 Metric)
C19 | CC0402KRX5R5BB105 | 1 | CAP CER 1UF 6.3V X5R 0402 | 1µF ±10% 6.3V Ceramic Capacitor X5R 0402 (1005 Metric)
C20 | CGA2B3X7R1H104K050BB | 1 | CAP CER 0.1UF 50V X7R 0402 | 0.1µF ±10% 50V Ceramic Capacitor X7R 0402 (1005 Metric)
C21 | CGA2B3X7R1H104K050BB | 1 | CAP CER 0.1UF 50V X7R 0402 | 0.1µF ±10% 50V Ceramic Capacitor X7R 0402 (1005 Metric)
C22 | CGA2B3X7R1H104K050BB | 1 | CAP CER 0.1UF 50V X7R 0402 | 0.1µF ±10% 50V Ceramic Capacitor X7R 0402 (1005 Metric)
C23 | CGA2B3X7R1H104K050BB | 1 | CAP CER 0.1UF 50V X7R 0402 | 0.1µF ±10% 50V Ceramic Capacitor X7R 0402 (1005 Metric)
C24 | GRM155R60J225ME15D | 1 | CAP CER 2.2UF 6.3V X5R 0402 | 2.2µF ±20% 6.3V Ceramic Capacitor X5R 0402 (1005 Metric)
C25 | 865080142007 | 1 | CAP ALUM 100 UF 20% 6.3 V SMD | 100µF 6.3V Aluminum Electrolytic Capacitors Radial, Can - SMD 2000 Hrs @ 105°C
C26 | 865080142007 | 1 | CAP ALUM 100 UF 20% 6.3 V SMD | 100µF 6.3V Aluminum Electrolytic Capacitors Radial, Can - SMD 2000 Hrs @ 105°C
C27 | CGA2B3X7R1H104K050BB | 1 | CAP CER 0.1UF 50V X7R 0402 | 0.1µF ±10% 50V Ceramic Capacitor X7R 0402 (1005 Metric)
C28 | CGA2B3X7R1H104K050BB | 1 | CAP CER 0.1UF 50V X7R 0402 | 0.1µF ±10% 50V Ceramic Capacitor X7R 0402 (1005 Metric)
C29 | CC0402JRNPO9BN330 | 1 | CAP CER 33PF 50V C0G/NPO 0402 | 33pF ±5% 50V Ceramic Capacitor C0G, NP0 0402 (1005 Metric)
C30 | CC0402JRNPO9BN330 | 1 | CAP CER 33PF 50V C0G/NPO 0402 | 33pF ±5% 50V Ceramic Capacitor C0G, NP0 0402 (1005 Metric)
C31 | C0402C100K5GACTU | 1 | CAP CER 10PF 50V C0G/NP0 0402 | 10pF ±10% 50V Ceramic Capacitor C0G, NP0 0402 (1005 Metric)
C32 | C0402C100K5GACTU | 1 | CAP CER 10PF 50V C0G/NP0 0402 | 10pF ±10% 50V Ceramic Capacitor C0G, NP0 0402 (1005 Metric)
C37 | CC0402JRNPO9BN101 | 1 | C 100pF 50V C0G, NP0 0402 | 100pF ±5% 50V Ceramic Capacitor C0G, NP0 0402 (1005 Metric)
C38 | 04023C103KAT2A | 1 | CAP CER 10nF 25V X7R 10% 0402 | Cap Cer 10nF 25V X7R 10% 0402
C39 | CGA2B3X7R1H104K050BB | 1 | CAP CER 0.1UF 50V X7R 0402 | 0.1µF ±10% 50V Ceramic Capacitor X7R 0402 (1005 Metric)
C40 | CC0402KRX7R7BB104 | 1 | CAP CER 0.1UF 16V X7R 0402 | 0.1µF ±10% 16V Ceramic Capacitor X7R 0402 (1005 Metric)
C41 | GRM188R61C106KAALJ | 1 | CAP CER 10UF 16V X5R 0603 | 10µF ±10% 16V Ceramic Capacitor X5R 0603 (1608 Metric)
C42 | GRM188R61C106KAALJ | 1 | CAP CER 10UF 16V X5R 0603 | 10µF ±10% 16V Ceramic Capacitor X5R 0603 (1608 Metric)
C43 | CC0402KRX7R7BB104 | 1 | CAP CER 0.1UF 16V X7R 0402 | 0.1µF ±10% 16V Ceramic Capacitor X7R 0402 (1005 Metric)
C44 | CGA2B3X7R1H104K050BB | 1 | CAP CER 0.1UF 50V X7R 0402 | 0.1µF ±10% 50V Ceramic Capacitor X7R 0402 (1005 Metric)
C45 | CGA2B3X7R1H104K050BB | 1 | CAP CER 0.1UF 50V X7R 0402 | 0.1µF ±10% 50V Ceramic Capacitor X7R 0402 (1005 Metric)
C46 | CC0402KRX5R5BB105 | 1 | CAP CER 1UF 6.3V X5R 0402 | 1µF ±10% 6.3V Ceramic Capacitor X5R 0402 (1005 Metric)
C47 | CC0402KRX5R5BB105 | 1 | CAP CER 1UF 6.3V X5R 0402 | 1µF ±10% 6.3V Ceramic Capacitor X5R 0402 (1005 Metric)
C50 | 04023C103KAT2A | 1 | CAP CER 10nF 25V X7R 10% 0402 | Cap Cer 10nF 25V X7R 10% 0402
C51 | C0402C102K5RACTU | 1 | CAP CER 1000PF 50V X7R 0402 | 1000pF ±10% 50V Ceramic Capacitor X7R 0402 (1005 Metric)
C52 | CC0402KRX5R5BB105 | 1 | CAP CER 1UF 6.3V X5R 0402 | 1µF ±10% 6.3V Ceramic Capacitor X5R 0402 (1005 Metric)
C53 | CGA2B2X7R1E223K050BA | 1 | CAP CER 0.022UF 25V X7R 0402 | 0.022µF ±10% 25V Ceramic Capacitor X7R 0402 (1005 Metric)
C54 | CC0805MKX5R8BB226 | 1 | CAP CER 22UF 25V X5R 0805 | 22µF ±20% 25V Ceramic Capacitor X5R 0805 (2012 Metric)
C55 | CC0603KRX5R7BB225 | 1 | CAP CER 2.2UF 16V X5R 0603 | 2.2µF ±10% 16V Ceramic Capacitor X5R 0603 (1608 Metric)
C56 | CC0402KRX5R5BB105 | 1 | CAP CER 1UF 6.3V X5R 0402 | 1µF ±10% 6.3V Ceramic Capacitor X5R 0402 (1005 Metric)
C61 | CC0805MKX5R8BB226 | 1 | CAP CER 22UF 25V X5R 0805 | 22µF ±20% 25V Ceramic Capacitor X5R 0805 (2012 Metric)
C62 | CC0402KRX7R7BB104 | 1 | CAP CER 0.1UF 16V X7R 0402 | 0.1µF ±10% 16V Ceramic Capacitor X7R 0402 (1005 Metric)
C63 | 04023C103KAT2A | 1 | CAP CER 10nF 25V X7R 10% 0402 | Cap Cer 10nF 25V X7R 10% 0402
C64 | CC0805MKX5R8BB226 | 1 | CAP CER 22UF 25V X5R 0805 | 22µF ±20% 25V Ceramic Capacitor X5R 0805 (2012 Metric)
C65 | CGA2B3X7R1H104K050BB | 1 | CAP CER 0.1UF 50V X7R 0402 | 0.1µF ±10% 50V Ceramic Capacitor X7R 0402 (1005 Metric)
C66 | CGA2B3X7R1H104K050BB | 1 | CAP CER 0.1UF 50V X7R 0402 | 0.1µF ±10% 50V Ceramic Capacitor X7R 0402 (1005 Metric)
C67 | CGA2B3X7R1H104K050BB | 1 | CAP CER 0.1UF 50V X7R 0402 | 0.1µF ±10% 50V Ceramic Capacitor X7R 0402 (1005 Metric)
C68 | CGA2B3X7R1H104K050BB | 1 | CAP CER 0.1UF 50V X7R 0402 | 0.1µF ±10% 50V Ceramic Capacitor X7R 0402 (1005 Metric)
C69 | CGA2B3X7R1H104K050BB | 1 | CAP CER 0.1UF 50V X7R 0402 | 0.1µF ±10% 50V Ceramic Capacitor X7R 0402 (1005 Metric)
C70 | CGA2B3X7R1H104K050BB | 1 | CAP CER 0.1UF 50V X7R 0402 | 0.1µF ±10% 50V Ceramic Capacitor X7R 0402 (1005 Metric)
C71 | GRM155R60J225ME15D | 1 | CAP CER 2.2UF 6.3V X5R 0402 | 2.2µF ±20% 6.3V Ceramic Capacitor X5R 0402 (1005 Metric)
C72 | CGA2B3X7R1H104K050BB | 1 | CAP CER 0.1UF 50V X7R 0402 | 0.1µF ±10% 50V Ceramic Capacitor X7R 0402 (1005 Metric)
C73 | CC0603MRX5R8BB105 | 1 | CAP CER 1UF 25V X5R 0603 | 1µF ±20% 25V Ceramic Capacitor X5R 0603 (1608 Metric)
C74 | CGA2B3X7R1H104K050BB | 1 | CAP CER 0.1UF 50V X7R 0402 | 0.1µF ±10% 50V Ceramic Capacitor X7R 0402 (1005 Metric)
C75 | CC0402KRX7R7BB104 | 1 | CAP CER 0.1UF 16V X7R 0402 | 0.1µF ±10% 16V Ceramic Capacitor X7R 0402 (1005 Metric)
C76 | CC0603KRX5R7BB475 | 1 | CAP CER 4.7UF 16V X5R 0603 | 4.7µF ±10% 16V Ceramic Capacitor X5R 0603 (1608 Metric)
C77 | CC0603KRX5R7BB475 | 1 | CAP CER 4.7UF 16V X5R 0603 | 4.7µF ±10% 16V Ceramic Capacitor X5R 0603 (1608 Metric)
C78 | CC0402KRX7R7BB104 | 1 | CAP CER 0.1UF 16V X7R 0402 | 0.1µF ±10% 16V Ceramic Capacitor X7R 0402 (1005 Metric)
C79 | GRM188R61C106KAALJ | 1 | CAP CER 10UF 16V X5R 0603 | 10µF ±10% 16V Ceramic Capacitor X5R 0603 (1608 Metric)
C80 | CC0402KRX7R7BB104 | 1 | CAP CER 0.1UF 16V X7R 0402 | 0.1µF ±10% 16V Ceramic Capacitor X7R 0402 (1005 Metric)
C88 | CC0402KRX5R7BB105 | 1 | CAP CER 1UF 16V X5R 0402 | 1µF ±10% 16V Ceramic Capacitor X5R 0402 (1005 Metric)
C89 | CGA2B3X7R1H104K050BB | 1 | CAP CER 0.1UF 50V X7R 0402 | 0.1µF ±10% 50V Ceramic Capacitor X7R 0402 (1005 Metric)
C90 | GRM188R61C106KAALJ | 1 | CAP CER 10UF 16V X5R 0603 | 10µF ±10% 16V Ceramic Capacitor X5R 0603 (1608 Metric)
C91 | CGA2B3X7R1H104K050BB | 1 | CAP CER 0.1UF 50V X7R 0402 | 0.1µF ±10% 50V Ceramic Capacitor X7R 0402 (1005 Metric)
C92 | CL21B106KOQNNNG | 1 | CAP CER 10UF 16V X7R 0805 | 10µF ±10% 16V Ceramic Capacitor X7R 0805 (2012 Metric)
C93 | GRM188R61C106KAALJ | 1 | CAP CER 10UF 16V X5R 0603 | 10µF ±10% 16V Ceramic Capacitor X5R 0603 (1608 Metric)
C94 | GRM188R61C106KAALJ | 1 | CAP CER 10UF 16V X5R 0603 | 10µF ±10% 16V Ceramic Capacitor X5R 0603 (1608 Metric)
C95 | CC0402KRX7R9BB221 | 1 | CAP CER 220PF 50V X7R 0402 | 220pF ±10% 50V Ceramic Capacitor X7R 0402 (1005 Metric)
C96 | C2012X7R1V475K125AC | 1 | CAP CER 4.7UF 35V X7R 0805 | CAP CER 4.7UF 35V X7R 0805
C97 | CC0402KRX7R9BB221 | 1 | CAP CER 220PF 50V X7R 0402 | 220pF ±10% 50V Ceramic Capacitor X7R 0402 (1005 Metric)
C98 | GRM21BR71A106KA73L | 1 | CAP CER 10uF X7R 10% 0805 | Capacitor,10uF,10V,X7R,10%,0805,Murata
C99 | CGA2B3X7R1H104K050BB | 1 | CAP CER 0.1UF 50V X7R 0402 | 0.1µF ±10% 50V Ceramic Capacitor X7R 0402 (1005 Metric)
C100 | CGA2B3X7R1H104K050BB | 1 | CAP CER 0.1UF 50V X7R 0402 | 0.1µF ±10% 50V Ceramic Capacitor X7R 0402 (1005 Metric)
C101 | CGA2B3X7R1H104K050BB | 1 | CAP CER 0.1UF 50V X7R 0402 | 0.1µF ±10% 50V Ceramic Capacitor X7R 0402 (1005 Metric)
C102 | CGA2B3X7R1H104K050BB | 1 | CAP CER 0.1UF 50V X7R 0402 | 0.1µF ±10% 50V Ceramic Capacitor X7R 0402 (1005 Metric)
C103 | CGA2B3X7R1H104K050BB | 1 | CAP CER 0.1UF 50V X7R 0402 | 0.1µF ±10% 50V Ceramic Capacitor X7R 0402 (1005 Metric)
C104 | CGA2B3X7R1H104K050BB | 1 | CAP CER 0.1UF 50V X7R 0402 | 0.1µF ±10% 50V Ceramic Capacitor X7R 0402 (1005 Metric)
C105 | CC0402KRX5R7BB105 | 1 | CAP CER 1UF 16V X5R 0402 | 1µF ±10% 16V Ceramic Capacitor X5R 0402 (1005 Metric)
C106 | CGA2B3X7R1H104K050BB | 1 | CAP CER 0.1UF 50V X7R 0402 | 0.1µF ±10% 50V Ceramic Capacitor X7R 0402 (1005 Metric)
C107 | CC0402KRX5R7BB105 | 1 | CAP CER 1UF 16V X5R 0402 | 1µF ±10% 16V Ceramic Capacitor X5R 0402 (1005 Metric)
C108 | CGA2B3X7R1H104K050BB | 1 | CAP CER 0.1UF 50V X7R 0402 | 0.1µF ±10% 50V Ceramic Capacitor X7R 0402 (1005 Metric)
C109 | CGA2B3X7R1H104K050BB | 1 | CAP CER 0.1UF 50V X7R 0402 | 0.1µF ±10% 50V Ceramic Capacitor X7R 0402 (1005 Metric)
C110 | CGA2B3X7R1H104K050BB | 1 | CAP CER 0.1UF 50V X7R 0402 | 0.1µF ±10% 50V Ceramic Capacitor X7R 0402 (1005 Metric)
C111 | CGA2B3X7R1H104K050BB | 1 | CAP CER 0.1UF 50V X7R 0402 | 0.1µF ±10% 50V Ceramic Capacitor X7R 0402 (1005 Metric)
C112 | CGA2B3X7R1H104K050BB | 1 | CAP CER 0.1UF 50V X7R 0402 | 0.1µF ±10% 50V Ceramic Capacitor X7R 0402 (1005 Metric)
C113 | GRM155R60J225ME15D | 1 | CAP CER 2.2UF 6.3V X5R 0402 | 2.2µF ±20% 6.3V Ceramic Capacitor X5R 0402 (1005 Metric)
C114 | CGA2B3X7R1H104K050BB | 1 | CAP CER 0.1UF 50V X7R 0402 | 0.1µF ±10% 50V Ceramic Capacitor X7R 0402 (1005 Metric)
C115 | GRM155R60J225ME15D | 1 | CAP CER 2.2UF 6.3V X5R 0402 | 2.2µF ±20% 6.3V Ceramic Capacitor X5R 0402 (1005 Metric)
C116 | CGA2B3X7R1H104K050BB | 1 | CAP CER 0.1UF 50V X7R 0402 | 0.1µF ±10% 50V Ceramic Capacitor X7R 0402 (1005 Metric)
C117 | GRM155R60J225ME15D | 1 | CAP CER 2.2UF 6.3V X5R 0402 | 2.2µF ±20% 6.3V Ceramic Capacitor X5R 0402 (1005 Metric)
C118 | CGA2B3X7R1H104K050BB | 1 | CAP CER 0.1UF 50V X7R 0402 | 0.1µF ±10% 50V Ceramic Capacitor X7R 0402 (1005 Metric)
C119 | CGA2B3X7R1H104K050BB | 1 | CGA2B3X7R1H104K050BB | 0.1µF ±10% 50V Ceramic Capacitor X7R 0402 (1005 Metric)
C120 | CGA2B3X7R1H104K050BB | 1 | CAP CER 0.1UF 50V X7R 0402 | 0.1µF ±10% 50V Ceramic Capacitor X7R 0402 (1005 Metric)
C121 | GRM188R6YA225KA12D | 1 | CAP CER 2.2UF 35V X5R 0603 | 2.2µF ±10% 35V Ceramic Capacitor X5R 0603 (1608 Metric)
C122 | CC0402KRX7R7BB104 | 1 | CAP CER 0.1UF 16V X7R 0402 | 0.1µF ±10% 16V Ceramic Capacitor X7R 0402 (1005 Metric)
C123 | GRM188R6YA225KA12D | 1 | CAP CER 2.2UF 35V X5R 0603 | 2.2µF ±10% 35V Ceramic Capacitor X5R 0603 (1608 Metric)
C124 | CGA2B3X7R1H104K050BB | 1 | CAP CER 0.1UF 50V X7R 0402 | 0.1µF ±10% 50V Ceramic Capacitor X7R 0402 (1005 Metric)
C125 | CC0402KRX7R7BB104 | 1 | CAP CER 0.1UF 16V X7R 0402 | 0.1µF ±10% 16V Ceramic Capacitor X7R 0402 (1005 Metric)
C126 | CC0402KRX7R7BB104 | 1 | CAP CER 0.1UF 16V X7R 0402 | 0.1µF ±10% 16V Ceramic Capacitor X7R 0402 (1005 Metric)
C127 | CPH3225A | 1 | CAP 11MF 3.3V SURFACE MNT | 11mF (EDLC) Supercapacitor 3.3V 1210 (3225 Metric)
C128 | CGA2B3X7R1H104K050BB | 1 | CAP CER 0.1UF 50V X7R 0402 | 0.1µF ±10% 50V Ceramic Capacitor X7R 0402 (1005 Metric)
C129 | CGA2B3X7R1H104K050BB | 1 | CAP CER 0.1UF 50V X7R 0402 | 0.1µF ±10% 50V Ceramic Capacitor X7R 0402 (1005 Metric)
C130 | CC0805MKX5R8BB226 | 1 | CAP CER 22UF 25V X5R 0805 | 22µF ±20% 25V Ceramic Capacitor X5R 0805 (2012 Metric)
C131 | CGA2B3X7R1H104K050BB | 1 | CAP CER 0.1UF 50V X7R 0402 | 0.1µF ±10% 50V Ceramic Capacitor X7R 0402 (1005 Metric)
C132 | C0402C182J5RACTU | 1 | CAP CER 1800PF 50V X7R 0402 | 1800pF ±5% 50V Ceramic Capacitor X7R 0402 (1005 Metric)
C133 | CC0402KRX5R7BB105 | 1 | CAP CER 1UF 16V X5R 0402 | 1µF ±10% 16V Ceramic Capacitor X5R 0402 (1005 Metric)
C134 | CL21B106KOQNNNG | 1 | CAP CER 10UF 16V X7R 0805 | 10µF ±10% 16V Ceramic Capacitor X7R 0805 (2012 Metric)
C135 | CL21B106KOQNNNG | 1 | CAP CER 10UF 16V X7R 0805 | 10µF ±10% 16V Ceramic Capacitor X7R 0805 (2012 Metric)
C136 | CC0805MKX5R8BB226 | 1 | CAP CER 22UF 25V X5R 0805 | 22µF ±20% 25V Ceramic Capacitor X5R 0805 (2012 Metric)
C137 | CC0805MKX5R8BB226 | 1 | CAP CER 22UF 25V X5R 0805 | 22µF ±20% 25V Ceramic Capacitor X5R 0805 (2012 Metric)
C138 | CC0805MKX5R8BB226 | 1 | CAP CER 22UF 25V X5R 0805 | 22µF ±20% 25V Ceramic Capacitor X5R 0805 (2012 Metric)
C139 | CC0402KRX5R7BB105 | 1 | CAP CER 1UF 16V X5R 0402 | 1µF ±10% 16V Ceramic Capacitor X5R 0402 (1005 Metric)
C140 | CGA2B3X7R1H104K050BB | 1 | CAP CER 0.1UF 50V X7R 0402 | 0.1µF ±10% 50V Ceramic Capacitor X7R 0402 (1005 Metric)
C141 | CGA2B3X7R1H104K050BB | 1 | CAP CER 0.1UF 50V X7R 0402 | 0.1µF ±10% 50V Ceramic Capacitor X7R 0402 (1005 Metric)
C142 | CGA2B3X7R1H104K050BB | 1 | CAP CER 0.1UF 50V X7R 0402 | 0.1µF ±10% 50V Ceramic Capacitor X7R 0402 (1005 Metric)
C143 | CC0402KRX5R7BB105 | 1 | CAP CER 1UF 16V X5R 0402 | 1µF ±10% 16V Ceramic Capacitor X5R 0402 (1005 Metric)
C144 | CGA2B3X7R1H104K050BB | 1 | CAP CER 0.1UF 50V X7R 0402 | 0.1µF ±10% 50V Ceramic Capacitor X7R 0402 (1005 Metric)
C145 | GRM155R60J225ME15D | 1 | CAP CER 2.2UF 6.3V X5R 0402 | 2.2µF ±20% 6.3V Ceramic Capacitor X5R 0402 (1005 Metric)
C146 | GRM155R60J225ME15D | 1 | CAP CER 2.2UF 6.3V X5R 0402 | 2.2µF ±20% 6.3V Ceramic Capacitor X5R 0402 (1005 Metric)
C147 | CGA2B3X7R1H104K050BB | 1 | CAP CER 0.1UF 50V X7R 0402 | 0.1µF ±10% 50V Ceramic Capacitor X7R 0402 (1005 Metric)
C148 | CGA2B3X7R1H104K050BB | 1 | CAP CER 0.1UF 50V X7R 0402 | 0.1µF ±10% 50V Ceramic Capacitor X7R 0402 (1005 Metric)
D1 | ESDA7P120-1U1M | 1 | ESDA7P120-1U1M | 11.5V Clamp 120A (8/20µs) Ipp Tvs Diode Surface Mount 1610
D2 | ESDA7P120-1U1M | 1 | ESDA7P120-1U1M | 11.5V Clamp 120A (8/20µs) Ipp Tvs Diode Surface Mount 1610
D3 | ESDA7P120-1U1M | 1 | ESDA7P120-1U1M | 11.5V Clamp 120A (8/20µs) Ipp Tvs Diode Surface Mount 1610
D4 | NSR0140P2T5G | 1 | NSR0140P2T5G | Diode Schottky 30V 70mA (DC) Surface Mount SOD-923
D5 | SMF05CT1G | 1 | SMF05CT1G | 12.5V Clamp 8A (8/20µs) Ipp Tvs Diode Surface Mount SC-88/SC70-6/SOT-363
D6 | SMF05CT1G | 1 | SMF05CT1G | 12.5V Clamp 8A (8/20µs) Ipp Tvs Diode Surface Mount SC-88/SC70-6/SOT-363
D7 | SR05-02CTG | 1 | SR05-02CTG | TVS DIODE 5VWM 18VC SOT143
D8 | NSR0140P2T5G | 1 | NSR0140P2T5G | Diode Schottky 30V 70mA (DC) Surface Mount SOD-923
D9 | ESDA7P120-1U1M | 1 | ESDA7P120-1U1M | 11.5V Clamp 120A (8/20µs) Ipp Tvs Diode Surface Mount 1610
D10 | NSR0140P2T5G | 1 | NSR0140P2T5G | Diode Schottky 30V 70mA (DC) Surface Mount SOD-923
D11 | LTST-C191KGKT | 1 | RESERVED | Green 571nm LED Indication - Discrete 2V 0603 (1608 Metric)
D12 | MM3Z5V1C | 1 | MM3Z5V1C | Zener Diode 5.1V 200mW ±5% Surface Mount SOD-323F
D13 | LTST-C191KRKT | 1 | LED RED CLEAR 0603 SMD | Red 631nm LED Indication - Discrete 2V 0603 (1608 Metric)
D14 | LTST-C191KGKT | 1 | LED GREEN CLEAR 0603 SMD | Green 571nm LED Indication - Discrete 2V 0603 (1608 Metric)
D15 | LTST-C191TBKT | 1 | LED BLUE CLEAR 0603 SMD | Blue 470nm LED Indication - Discrete 3.3V 0603 (1608 Metric)
D16 | ESDA7P120-1U1M | 1 | ESDA7P120-1U1M | 11.5V Clamp 120A (8/20µs) Ipp Tvs Diode Surface Mount 1610
D17 | SMF05CT1G | 1 | SMF05CT1G | 12.5V Clamp 8A (8/20µs) Ipp Tvs Diode Surface Mount SC-88/SC70-6/SOT-363
D18 | LTST-C191KGKT | 1 | +3V3 | Green 571nm LED Indication - Discrete 2V 0603 (1608 Metric)
D19 | STPS120MF | 1 | STPS120MF | Diode Schottky 20V 1A Surface Mount STmite Flat
D20 | MMSZ5226B-7-F | 1 | MMSZ5226B-7-F | Zener Diode ±5% Surface Mount SOD-123
D21 | ESDA25P35-1U1M | 1 | ESDA25P35-1U1M | 41V Clamp 35A (8/20µs) Ipp Tvs Diode Surface Mount 1610
D22 | NSR0140P2T5G | 1 | NSR0140P2T5G | Diode Schottky 30V 70mA (DC) Surface Mount SOD-923
D23 | PMEG4050EP,115 | 1 | PMEG4050EP,115 | Diode Schottky 40V 5A Surface Mount CFP5
D24 | SMF05CT1G | 1 | SMF05CT1G | 12.5V Clamp 8A (8/20µs) Ipp Tvs Diode Surface Mount SC-88/SC70-6/SOT-363
D25 | SMF05CT1G | 1 | SMF05CT1G | 12.5V Clamp 8A (8/20µs) Ipp Tvs Diode Surface Mount SC-88/SC70-6/SOT-363
ESP32_MOD | ESP32-WROOM-32D | 1 | ESP32-WROOM-32D | Bluetooth, WiFi 802.11b/g/n, Bluetooth v4.2 + EDR, Class 1, 2 and 3 Transceiver Module 2.4GHz ~ 2.5GHz Integrated, Trace Surface Mount
FB1 | MPZ1608S300ATAH0 | 1 | Not Fitted in BG95-M3_Global Variant | 30 Ohms @ 100MHz 1 Power Line Ferrite Bead 0603 (1608 Metric) 5A 10mOhm
FB2 | MPZ1608S300ATAH0 | 1 | MPZ1608S300ATAH0 | 30 Ohms @ 100MHz 1 Power Line Ferrite Bead 0603 (1608 Metric) 5A 10mOhm
FB3 | MPZ1608S300ATAH0 | 1 | MPZ1608S300ATAH0 | 30 Ohms @ 100MHz 1 Power Line Ferrite Bead 0603 (1608 Metric) 5A 10mOhm
FB4 | BLM18EG471SN1D | 1 | FERRITE BEAD 470 OHM 0603 1LN | 470 Ohms @ 100MHz 1 Ferrite Bead 0603 (1608 Metric) 500mA 210mOhm
FB5 | BLM15AX102SN1D | 1 | FERRITE BEAD 1 KOHM 0402 1LN | 1 kOhms @ 100MHz 1 Ferrite Bead 0402 (1005 Metric) 350mA 490mOhm
FB6 | BLM15AX102SN1D | 1 | FERRITE BEAD 1 KOHM 0402 1LN | 1 kOhms @ 100MHz 1 Ferrite Bead 0402 (1005 Metric) 350mA 490mOhm
L1 | IHLP1212BZER1R0M11 | 1 | FIXED IND 1UH 5A 24 MOHM SMD | 1µH Shielded Molded Inductor 5A 24mOhm Max Nonstandard
L3 | 74438323010 | 1 | FIXED IND 1UH 2.5A 75 MOHM SMD | 1µH Shielded Molded Inductor 2.5A 75mOhm Max 1008 (2520 Metric)
L4 | LPD5030-682MR | 1 | FIXED IND COUIPLED 6.8UH 1.2A 160 mOHM SMD | 6.8µH Shielded Coupled Inductors 1.2A 160mOhm Max 1919 (4.8x4.8 Metric)
L5 | MSD1048H-222 | 1 | FIXED IND COUIPLED 2.2UH 3.2A 22 MOHM SMD | 2.2µH Shielded Coupled Inductors 3.2A 22mOhm Max 4040 (10.3x10.3 Metric)
LD1 | 150066M153000 | 1 | 150066M153000 | Red, Green, Blue (RGB) 624nm Red, 525nm Green, 470nm Blue LED Indication - Discrete 2V Red, 3.3V Green, 3.3V Blue 0606 (1616 Metric)
P09 | LTST-C191KSKT | 1 | "PWR" | Yellow 591nm LED Indication - Discrete 2.1V 0603 (1608 Metric)
P10 | 201267-0005 | 1 | USB | USB-C (USB TYPE-C) USB 3.2 Gen 2 (USB 3.1 Gen 2, Superspeed + (USB 3.1)) Receptacle Connector 24 Position Surface Mount, Right Angle; Through Hole
P15 | LTST-C191TBKT | 1 | "ON" | Blue 470nm LED Indication - Discrete 3.3V 0603 (1608 Metric)
P16 | S4B-ZR(LF)(SN) | 1 | DC Motor | Connector Header Through Hole, Right Angle 4 position 0.059" (1.50mm)
P18 | S3B-ZR(LF)(SN) | 1 | BATT | Connector Header Through Hole, Right Angle 3 position 0.059" (1.50mm)
P19 | ERT-J1VG103JA | 1 | THERMISTOR NTC 10KOHM 3380K 0603 | NTC Thermistor 10k 0603 (1608 Metric)
P19.1 | S2B-ZR(LF)(SN) | 1 | "Batt Temp" | Connector Header Through Hole, Right Angle 2 position 0.059" (1.50mm)
P20 | 0545500571 | 1 | S201 | 5 Position FFC, FPC Connector Contacts, Top 0.020" (0.50mm) Surface Mount, Right Angle
P22 | S5B-ZR(LF)(SN) | 1 | BLDC I2C | Connector Header Through Hole, Right Angle 5 position 0.059" (1.50mm)
P23 | LTST-C191KRKT | 1 | "SYS_FAULT" | Red 631nm LED Indication - Discrete 2V 0603 (1608 Metric)
P24 | SMT-0440-S-R | 1 | BUZZ | Buzzers Transducer, Externally Driven 90mA 4kHz 70dB @ 3V, 10cm Surface Mount Solder Pads
P25 | S4B-ZR(LF)(SN) | 1 | Stepper Motor | Connector Header Through Hole, Right Angle 4 position 0.059" (1.50mm)
P28 | 0545500571 | 1 | S202 | 5 Position FFC, FPC Connector Contacts, Top 0.020" (0.50mm) Surface Mount, Right Angle
P102 | 5025700893 | 1 | uSD Card | 10 (8 + 2) Position Card Connector Secure Digital - microSD™ Surface Mount, Right Angle Gold
Q1 | DMN32D2LV-7 | 1 | DMN32D2LV-7 | Mosfet Array 2 N-Channel (Dual) 30V 400mA 400mW Surface Mount SOT-563
Q2 | BSS816NWH6327XTSA1 | 1 | BSS816NWH6327XTSA1 | N-Channel 20V 1.4A (Ta) 500mW (Ta) Surface Mount PG-SOT323-3
Q3 | DTC143ZET1G | 1 | DTC143ZET1G | Pre-Biased Bipolar Transistor (BJT) NPN - Pre-Biased 50V 100mA 200mW Surface Mount SC-75, SOT-416
Q4 | DTC143ZET1G | 1 | DTC143ZET1G | Pre-Biased Bipolar Transistor (BJT) NPN - Pre-Biased 50V 100mA 200mW Surface Mount SC-75, SOT-416
Q5 | DTC143ZET1G | 1 | DTC143ZET1G | Pre-Biased Bipolar Transistor (BJT) NPN - Pre-Biased 50V 100mA 200mW Surface Mount SC-75, SOT-416
Q6 | DTC143ZET1G | 1 | DTC143ZET1G | Pre-Biased Bipolar Transistor (BJT) NPN - Pre-Biased 50V 100mA 200mW Surface Mount SC-75, SOT-416
Q7 | DTC143ZET1G | 1 | DTC143ZET1G | Pre-Biased Bipolar Transistor (BJT) NPN - Pre-Biased 50V 100mA 200mW Surface Mount SC-75, SOT-416
Q8 | DTC143ZET1G | 1 | DTC143ZET1G | Pre-Biased Bipolar Transistor (BJT) NPN - Pre-Biased 50V 100mA 200mW Surface Mount SC-75, SOT-416
Q9 | DMN32D2LV-7 | 1 | DMN32D2LV-7 | Mosfet Array 2 N-Channel (Dual) 30V 400mA 400mW Surface Mount SOT-563
Q10 | BC847CW,115 | 1 | BC847CW,115 | Bipolar (BJT) Transistor NPN 45V 100mA 100MHz 200mW Surface Mount SOT-323-3
Q11 | BC847CW,115 | 1 | BC847CW,115 | Bipolar (BJT) Transistor NPN 45V 100mA 100MHz 200mW Surface Mount SOT-323-3
Q12 | DMN32D2LV-7 | 1 | DMN32D2LV-7 | Mosfet Array 2 N-Channel (Dual) 30V 400mA 400mW Surface Mount SOT-563
Q13 | EM6M2T2R | 1 | EM6M2T2R | Mosfet Array N and P-Channel 20V 200mA 150mW Surface Mount EMT6
Q14 | BC847CW,115 | 1 | BC847CW,115 | Bipolar (BJT) Transistor NPN 45V 100mA 100MHz 200mW Surface Mount SOT-323-3
R1 | RC0402FR-0710KP | 1 | RES SMD 10K OHM 1% 1/16W 0402 | 10 kOhms ±1% 0.063W, 1/16W Chip Resistor 0402 (1005 Metric) Moisture Resistant Thick Film
R2 | RC0402FR-0731K6L | 1 | RES SMD 31.6K OHM 1% 1/16W 0402 | 31.6 kOhms ±1% 0.063W, 1/16W Chip Resistor 0402 (1005 Metric) Moisture Resistant Thick Film
R3 | RC0402FR-075K36L | 1 | RES SMD 5.36K OHM 1% 1/16W 0402 | 5.36 kOhms ±1% 0.063W, 1/16W Chip Resistor 0402 (1005 Metric) Moisture Resistant Thick Film
R4 | RC0402FR-0710KP | 1 | RES SMD 10K OHM 1% 1/16W 0402 | 10 kOhms ±1% 0.063W, 1/16W Chip Resistor 0402 (1005 Metric) Moisture Resistant Thick Film
R5 | RC0402FR-072K7L | 1 | RES SMD 2.7K OHM 1% 1/16W 0402 | 2.7 kOhms ±1% 0.063W, 1/16W Chip Resistor 0402 (1005 Metric) Moisture Resistant Thick Film
R6 | RC0402FR-072K7L | 1 | RES SMD 2.7K OHM 1% 1/16W 0402 | 2.7 kOhms ±1% 0.063W, 1/16W Chip Resistor 0402 (1005 Metric) Moisture Resistant Thick Film
R7 | RC0402FR-07100KL | 1 | RES SMD 100K OHM 1% 1/16W 0402 | 100 kOhms ±1% 0.063W, 1/16W Chip Resistor 0402 (1005 Metric) Moisture Resistant Thick Film
R8 | RC0402FR-07100KL | 1 | RES SMD 100K OHM 1% 1/16W 0402 | 100 kOhms ±1% 0.063W, 1/16W Chip Resistor 0402 (1005 Metric) Moisture Resistant Thick Film
R9 | RC0402FR-07100KL | 1 | RES SMD 100K OHM 1% 1/16W 0402 | 100 kOhms ±1% 0.063W, 1/16W Chip Resistor 0402 (1005 Metric) Moisture Resistant Thick Film
R10 | RC0402FR-07100KL | 1 | RES SMD 100K OHM 1% 1/16W 0402 | 100 kOhms ±1% 0.063W, 1/16W Chip Resistor 0402 (1005 Metric) Moisture Resistant Thick Film
R11 | RC0402FR-07100KL | 1 | RES SMD 100K OHM 1% 1/16W 0402 | 100 kOhms ±1% 0.063W, 1/16W Chip Resistor 0402 (1005 Metric) Moisture Resistant Thick Film
R12 | RC0402FR-07100KL | 1 | RES SMD 100K OHM 1% 1/16W 0402 | 100 kOhms ±1% 0.063W, 1/16W Chip Resistor 0402 (1005 Metric) Moisture Resistant Thick Film
R13 | RC0402FR-07100KL | 1 | RES SMD 100K OHM 1% 1/16W 0402 | 100 kOhms ±1% 0.063W, 1/16W Chip Resistor 0402 (1005 Metric) Moisture Resistant Thick Film
R14 | RC0402FR-07100KL | 1 | RES SMD 100K OHM 1% 1/16W 0402 | 100 kOhms ±1% 0.063W, 1/16W Chip Resistor 0402 (1005 Metric) Moisture Resistant Thick Film
R15 | RC0402FR-07100KL | 1 | RES SMD 100K OHM 1% 1/16W 0402 | 100 kOhms ±1% 0.063W, 1/16W Chip Resistor 0402 (1005 Metric) Moisture Resistant Thick Film
R16 | RC0402FR-07100KL | 1 | RES SMD 100K OHM 1% 1/16W 0402 | 100 kOhms ±1% 0.063W, 1/16W Chip Resistor 0402 (1005 Metric) Moisture Resistant Thick Film
R17 | RC0402FR-07100KL | 1 | RES SMD 100K OHM 1% 1/16W 0402 | 100 kOhms ±1% 0.063W, 1/16W Chip Resistor 0402 (1005 Metric) Moisture Resistant Thick Film
R18 | RC0402JR-070RL | 1 | RES SMD 0 OHM JUMPER 1/16W 0402 | 0 Ohms Jumper 0.063W, 1/16W Chip Resistor 0402 (1005 Metric) Moisture Resistant Thick Film
R19 | RC0402JR-070RL | 1 | RES SMD 0 OHM JUMPER 1/16W 0402 | 0 Ohms Jumper 0.063W, 1/16W Chip Resistor 0402 (1005 Metric) Moisture Resistant Thick Film
R20 | AC0402FR-0710RL | 1 | RES SMD 10 OHM 1% 1/16W 0402 | 10 Ohms ±1% 0.063W, 1/16W Chip Resistor 0402 (1005 Metric) Automotive AEC-Q200, Moisture Resistant Thick Film
R21 | RC0402FR-0710KP | 1 | RES SMD 10K OHM 1% 1/16W 0402 | 10 kOhms ±1% 0.063W, 1/16W Chip Resistor 0402 (1005 Metric) Moisture Resistant Thick Film
R22 | RC0402JR-070RL | 1 | RES SMD 0 OHM JUMPER 1/16W 0402 | 0 Ohms Jumper 0.063W, 1/16W Chip Resistor 0402 (1005 Metric) Moisture Resistant Thick Film
R23 | RC0402JR-070RL | 1 | RES SMD 0 OHM JUMPER 1/16W 0402 | 0 Ohms Jumper 0.063W, 1/16W Chip Resistor 0402 (1005 Metric) Moisture Resistant Thick Film
R24 | RC0402FR-0710KP | 1 | RES SMD 10K OHM 1% 1/16W 0402 | 10 kOhms ±1% 0.063W, 1/16W Chip Resistor 0402 (1005 Metric) Moisture Resistant Thick Film
R25 | RC0402FR-0710KP | 1 | RES SMD 10K OHM 1% 1/16W 0402 | 10 kOhms ±1% 0.063W, 1/16W Chip Resistor 0402 (1005 Metric) Moisture Resistant Thick Film
R26 | RC0402FR-0710KP | 1 | RES SMD 10K OHM 1% 1/16W 0402 | 10 kOhms ±1% 0.063W, 1/16W Chip Resistor 0402 (1005 Metric) Moisture Resistant Thick Film
R29 | RC0402JR-070RL | 1 | RES SMD 0 OHM JUMPER 1/16W 0402 | 0 Ohms Jumper 0.063W, 1/16W Chip Resistor 0402 (1005 Metric) Moisture Resistant Thick Film
R31 | RC0402FR-0710KP | 1 | RES SMD 10K OHM 1% 1/16W 0402 | 10 kOhms ±1% 0.063W, 1/16W Chip Resistor 0402 (1005 Metric) Moisture Resistant Thick Film
R32 | RC0402FR-07402RL | 1 | RES SMD 402 OHM 1% 1/16W 0402 | 402 Ohms ±1% 0.063W, 1/16W Chip Resistor 0402 (1005 Metric) Moisture Resistant Thick Film
R33 | RC0402FR-07402RL | 1 | RES SMD 402 OHM 1% 1/16W 0402 | 402 Ohms ±1% 0.063W, 1/16W Chip Resistor 0402 (1005 Metric) Moisture Resistant Thick Film
R34 | RC0402FR-07402RL | 1 | RES SMD 402 OHM 1% 1/16W 0402 | 402 Ohms ±1% 0.063W, 1/16W Chip Resistor 0402 (1005 Metric) Moisture Resistant Thick Film
R35 | RC0402FR-07402RL | 1 | RES SMD 402 OHM 1% 1/16W 0402 | 402 Ohms ±1% 0.063W, 1/16W Chip Resistor 0402 (1005 Metric) Moisture Resistant Thick Film
R36 | RC0402JR-070RL | 1 | RES SMD 0 OHM JUMPER 1/16W 0402 | 0 Ohms Jumper 0.063W, 1/16W Chip Resistor 0402 (1005 Metric) Moisture Resistant Thick Film
R37 | RC0402FR-0710KP | 1 | RES SMD 10K OHM 1% 1/16W 0402 | 10 kOhms ±1% 0.063W, 1/16W Chip Resistor 0402 (1005 Metric) Moisture Resistant Thick Film
R38 | RC0402FR-0710KP | 1 | RES SMD 10K OHM 1% 1/16W 0402 | 10 kOhms ±1% 0.063W, 1/16W Chip Resistor 0402 (1005 Metric) Moisture Resistant Thick Film
R39 | RC0402JR-070RL | 1 | RES SMD 0 OHM JUMPER 1/16W 0402 | 0 Ohms Jumper 0.063W, 1/16W Chip Resistor 0402 (1005 Metric) Moisture Resistant Thick Film
R42 | RC0402FR-0710KP | 1 | RES SMD 10K OHM 1% 1/16W 0402 | 10 kOhms ±1% 0.063W, 1/16W Chip Resistor 0402 (1005 Metric) Moisture Resistant Thick Film
R43 | RC0402FR-072KL | 1 | RES SMD 2K OHM 1% 1/16W 0402 | 2 kOhms ±1% 0.063W, 1/16W Chip Resistor 0402 (1005 Metric) Moisture Resistant Thick Film
R44 | RC0402FR-072KL | 1 | RES SMD 2K OHM 1% 1/16W 0402 | 2 kOhms ±1% 0.063W, 1/16W Chip Resistor 0402 (1005 Metric) Moisture Resistant Thick Film
R45 | RC0402FR-0710KP | 1 | RES SMD 10K OHM 1% 1/16W 0402 | 10 kOhms ±1% 0.063W, 1/16W Chip Resistor 0402 (1005 Metric) Moisture Resistant Thick Film
R46 | RC0402FR-072KL | 1 | RES SMD 2K OHM 1% 1/16W 0402 | 2 kOhms ±1% 0.063W, 1/16W Chip Resistor 0402 (1005 Metric) Moisture Resistant Thick Film
R47 | RC0402FR-0715KL | 1 | RES SMD 15K OHM 1% 1/16W 0402 | 15 kOhms ±1% 0.063W, 1/16W Chip Resistor 0402 (1005 Metric) Thick Film
R48 | RC0402JR-070RL | 1 | RES SMD 0 OHM JUMPER 1/16W 0402 | 0 Ohms Jumper 0.063W, 1/16W Chip Resistor 0402 (1005 Metric) Moisture Resistant Thick Film
R49 | RC0402JR-070RL | 1 | RES SMD 0 OHM JUMPER 1/16W 0402 | 0 Ohms Jumper 0.063W, 1/16W Chip Resistor 0402 (1005 Metric) Moisture Resistant Thick Film
R50 | RC0402JR-070RL | 1 | RES SMD 0 OHM JUMPER 1/16W 0402 | 0 Ohms Jumper 0.063W, 1/16W Chip Resistor 0402 (1005 Metric) Moisture Resistant Thick Film
R51 | RC0402JR-070RL | 1 | RES SMD 0 OHM JUMPER 1/16W 0402 | 0 Ohms Jumper 0.063W, 1/16W Chip Resistor 0402 (1005 Metric) Moisture Resistant Thick Film
R52 | RC0402JR-070RL | 1 | RES SMD 0 OHM JUMPER 1/16W 0402 | 0 Ohms Jumper 0.063W, 1/16W Chip Resistor 0402 (1005 Metric) Moisture Resistant Thick Film
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

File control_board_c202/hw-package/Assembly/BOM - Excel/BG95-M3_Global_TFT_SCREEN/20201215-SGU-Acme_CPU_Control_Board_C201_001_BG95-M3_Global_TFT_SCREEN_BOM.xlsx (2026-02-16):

Designator | Manufacturer Part Number | Quantity | Comment | Description
B1, C127 | CPH3225A | 2 | CAP 11MF 3.3V SURFACE MNT | 11mF (EDLC) Supercapacitor 3.3V 1210 (3225 Metric)
BTN1, BTN2 | USLPT2819DT2TR | 2 | RESET, BOOT | Tactile Switch SPST-NO Top Actuated Surface Mount
C1 | CC0603KRX5R7BB105 | 1 | CAP CER 1UF 16V X5R 0603 | 1µF ±10% 16V Ceramic Capacitor X5R 0603 (1608 Metric)
C2 | CGA2B3X7R1H473K050BB | 1 | CAP CER 0.047UF 50V X7R 0402 | 0.047µF ±10% 50V Ceramic Capacitor X7R 0402 (1005 Metric)
C3 | CC0603KRX5R6BB475 | 1 | CAP CER 4.7UF 10V X5R 0603 | 4.7µF ±10% 10V Ceramic Capacitor X5R 0603 (1608 Metric)
C4 | CC1206KKX7R8BB106 | 1 | CAP CER 10UF 25V X7R 1206 | 10µF ±10% 25V Ceramic Capacitor X7R 1206 (3216 Metric)
C5, C6, C7, C8, C57, C98 | GRM21BR71A106KA73L | 6 | CAP CER 10uF X7R 10% 0805 | Capacitor,10uF,10V,X7R,10%,0805,Murata
C9, C10, C17, C18, C20, C21, C22, C23, C27, C28, C39, C44, C45, C58, C65, C66, C67, C68, C69, C70, C72, C74, C89, C91, C99, C100, C101, C102, C103, C104, C106, C108, C109, C110, C111, C112, C114, C116, C118, C119, C120, C124, C128, C129, C131, C140, C141, C142, C144, C147, C148 | CGA2B3X7R1H104K050BB | 51 | CAP CER 0.1UF 50V X7R 0402, CGA2B3X7R1H104K050BB | 0.1µF ±10% 50V Ceramic Capacitor X7R 0402 (1005 Metric)
C11, C12 | AC0402CRNPO9BN5R6 | 2 | CAP CER 5.6PF 50V NPO 0402 | 5.6pF ±0.25pF 50V Ceramic Capacitor C0G, NP0 0402 (1005 Metric)
C13, C14, C15 | 865080443009 | 3 | CAP ALUM 68 UF 20% 25 V SMD | 68µF 25V Aluminum Electrolytic Capacitors Radial, Can - SMD 2000 Hrs @ 105°C
C16, C19, C46, C47, C52, C56 | CC0402KRX5R5BB105 | 6 | CAP CER 1UF 6.3V X5R 0402 | 1µF ±10% 6.3V Ceramic Capacitor X5R 0402 (1005 Metric)
C24, C71, C113, C115, C117, C145, C146 | GRM155R60J225ME15D | 7 | CAP CER 2.2UF 6.3V X5R 0402 | 2.2µF ±20% 6.3V Ceramic Capacitor X5R 0402 (1005 Metric)
C25, C26 | 865080142007 | 2 | CAP ALUM 100 UF 20% 6.3 V SMD | 100µF 6.3V Aluminum Electrolytic Capacitors Radial, Can - SMD 2000 Hrs @ 105°C
C29, C30 | CC0402JRNPO9BN330 | 2 | CAP CER 33PF 50V C0G/NPO 0402 | 33pF ±5% 50V Ceramic Capacitor C0G, NP0 0402 (1005 Metric)
C31, C32 | C0402C100K5GACTU | 2 | CAP CER 10PF 50V C0G/NP0 0402 | 10pF ±10% 50V Ceramic Capacitor C0G, NP0 0402 (1005 Metric)
C37 | CC0402JRNPO9BN101 | 1 | C 100pF 50V C0G, NP0 0402 | 100pF ±5% 50V Ceramic Capacitor C0G, NP0 0402 (1005 Metric)
C38, C50, C63 | 04023C103KAT2A | 3 | CAP CER 10nF 25V X7R 10% 0402 | Cap Cer 10nF 25V X7R 10% 0402
C40, C43, C62, C75, C78, C80, C122, C125, C126 | CC0402KRX7R7BB104 | 9 | CAP CER 0.1UF 16V X7R 0402 | 0.1µF ±10% 16V Ceramic Capacitor X7R 0402 (1005 Metric)
C41, C42, C79, C90, C93, C94 | GRM188R61C106KAALJ | 6 | CAP CER 10UF 16V X5R 0603 | 10µF ±10% 16V Ceramic Capacitor X5R 0603 (1608 Metric)
C51 | C0402C102K5RACTU | 1 | CAP CER 1000PF 50V X7R 0402 | 1000pF ±10% 50V Ceramic Capacitor X7R 0402 (1005 Metric)
C53 | CGA2B2X7R1E223K050BA | 1 | CAP CER 0.022UF 25V X7R 0402 | 0.022µF ±10% 25V Ceramic Capacitor X7R 0402 (1005 Metric)
C54, C61, C64, C130, C136, C137, C138 | CC0805MKX5R8BB226 | 7 | CAP CER 22UF 25V X5R 0805 | 22µF ±20% 25V Ceramic Capacitor X5R 0805 (2012 Metric)
C55 | CC0603KRX5R7BB225 | 1 | CAP CER 2.2UF 16V X5R 0603 | 2.2µF ±10% 16V Ceramic Capacitor X5R 0603 (1608 Metric)
C59, C60 | LMK212BJ226MG-T | 2 | CAP CER 22UF 10V X5R 0805 | 22µF ±20% 10V Ceramic Capacitor X5R 0805 (2012 Metric)
C73 | CC0603MRX5R8BB105 | 1 | CAP CER 1UF 25V X5R 0603 | 1µF ±20% 25V Ceramic Capacitor X5R 0603 (1608 Metric)
C76, C77 | CC0603KRX5R7BB475 | 2 | CAP CER 4.7UF 16V X5R 0603 | 4.7µF ±10% 16V Ceramic Capacitor X5R 0603 (1608 Metric)
C88, C105, C107, C133, C139, C143 | CC0402KRX5R7BB105 | 6 | CAP CER 1UF 16V X5R 0402 | 1µF ±10% 16V Ceramic Capacitor X5R 0402 (1005 Metric)
C92, C134, C135 | CL21B106KOQNNNG | 3 | CAP CER 10UF 16V X7R 0805 | 10µF ±10% 16V Ceramic Capacitor X7R 0805 (2012 Metric)
C95, C97 | CC0402KRX7R9BB221 | 2 | CAP CER 220PF 50V X7R 0402 | 220pF ±10% 50V Ceramic Capacitor X7R 0402 (1005 Metric)
C96 | C2012X7R1V475K125AC | 1 | CAP CER 4.7UF 35V X7R 0805 | CAP CER 4.7UF 35V X7R 0805
C121, C123 | GRM188R6YA225KA12D | 2 | CAP CER 2.2UF 35V X5R 0603 | 2.2µF ±10% 35V Ceramic Capacitor X5R 0603 (1608 Metric)
C132 | C0402C182J5RACTU | 1 | CAP CER 1800PF 50V X7R 0402 | 1800pF ±5% 50V Ceramic Capacitor X7R 0402 (1005 Metric)
D1, D2, D3, D9, D16 | ESDA7P120-1U1M | 5 | ESDA7P120-1U1M | 11.5V Clamp 120A (8/20µs) Ipp Tvs Diode Surface Mount 1610
D4, D8, D10, D22 | NSR0140P2T5G | 4 | NSR0140P2T5G | Diode Schottky 30V 70mA (DC) Surface Mount SOD-923
D5, D6, D17, D24, D25 | SMF05CT1G | 5 | SMF05CT1G | 12.5V Clamp 8A (8/20µs) Ipp Tvs Diode Surface Mount SC-88/SC70-6/SOT-363
D7 | SR05-02CTG | 1 | SR05-02CTG | TVS DIODE 5VWM 18VC SOT143
D11, D14, D18 | LTST-C191KGKT | 3 | RESERVED, LED GREEN CLEAR 0603 SMD, +3V3 | Green 571nm LED Indication - Discrete 2V 0603 (1608 Metric)
D12 | MM3Z5V1C | 1 | MM3Z5V1C | Zener Diode 5.1V 200mW ±5% Surface Mount SOD-323F
D13, P23 | LTST-C191KRKT | 2 | LED RED CLEAR 0603 SMD, "SYS_FAULT" | Red 631nm LED Indication - Discrete 2V 0603 (1608 Metric)
D15, P15 | LTST-C191TBKT | 2 | LED BLUE CLEAR 0603 SMD, "ON" | Blue 470nm LED Indication - Discrete 3.3V 0603 (1608 Metric)
D19 | STPS120MF | 1 | STPS120MF | Diode Schottky 20V 1A Surface Mount STmite Flat
D20 | MMSZ5226B-7-F | 1 | MMSZ5226B-7-F | Zener Diode ±5% Surface Mount SOD-123
D21 | ESDA25P35-1U1M | 1 | ESDA25P35-1U1M | 41V Clamp 35A (8/20µs) Ipp Tvs Diode Surface Mount 1610
D23 | PMEG4050EP,115 | 1 | PMEG4050EP,115 | Diode Schottky 40V 5A Surface Mount CFP5
ESP32_MOD | ESP32-WROOM-32D | 1 | ESP32-WROOM-32D | Bluetooth, WiFi 802.11b/g/n, Bluetooth v4.2 + EDR, Class 1, 2 and 3 Transceiver Module 2.4GHz ~ 2.5GHz Integrated, Trace Surface Mount
FB2, FB3 | MPZ1608S300ATAH0 | 2 | MPZ1608S300ATAH0 | 30 Ohms @ 100MHz 1 Power Line Ferrite Bead 0603 (1608 Metric) 5A 10mOhm
FB4 | BLM18EG471SN1D | 1 | FERRITE BEAD 470 OHM 0603 1LN | 470 Ohms @ 100MHz 1 Ferrite Bead 0603 (1608 Metric) 500mA 210mOhm
FB5, FB6 | BLM15AX102SN1D | 2 | FERRITE BEAD 1 KOHM 0402 1LN | 1 kOhms @ 100MHz 1 Ferrite Bead 0402 (1005 Metric) 350mA 490mOhm
L1 | IHLP1212BZER1R0M11 | 1 | FIXED IND 1UH 5A 24 MOHM SMD | 1µH Shielded Molded Inductor 5A 24mOhm Max Nonstandard
L2 | 74405031010 | 1 | FIXED IND 1UH 2.4A 54 MOHM MAX | 1µH Semi-Shielded Wirewound Inductor 2.4A 54mOhm Max Nonstandard
L3 | 74438323010 | 1 | FIXED IND 1UH 2.5A 75 MOHM SMD | 1µH Shielded Molded Inductor 2.5A 75mOhm Max 1008 (2520 Metric)
L4 | LPD5030-682MR | 1 | FIXED IND COUIPLED 6.8UH 1.2A 160 mOHM SMD | 6.8µH Shielded Coupled Inductors 1.2A 160mOhm Max 1919 (4.8x4.8 Metric)
L5 | MSD1048H-222 | 1 | FIXED IND COUIPLED 2.2UH 3.2A 22 MOHM SMD | 2.2µH Shielded Coupled Inductors 3.2A 22mOhm Max 4040 (10.3x10.3 Metric)
LD1 | 150066M153000 | 1 | 150066M153000 | Red, Green, Blue (RGB) 624nm Red, 525nm Green, 470nm Blue LED Indication - Discrete 2V Red, 3.3V Green, 3.3V Blue 0606 (1616 Metric)
P09 | LTST-C191KSKT | 1 | "PWR" | Yellow 591nm LED Indication - Discrete 2.1V 0603 (1608 Metric)
P10 | 201267-0005 | 1 | USB | USB-C (USB TYPE-C) USB 3.2 Gen 2 (USB 3.1 Gen 2, Superspeed + (USB 3.1)) Receptacle Connector 24 Position Surface Mount, Right Angle; Through Hole
P16, P25 | S4B-ZR(LF)(SN) | 2 | DC Motor, Stepper Motor | Connector Header Through Hole, Right Angle 4 position 0.059" (1.50mm)
P18 | S3B-ZR(LF)(SN) | 1 | BATT | Connector Header Through Hole, Right Angle 3 position 0.059" (1.50mm)
P19 | ERT-J1VG103JA | 1 | THERMISTOR NTC 10KOHM 3380K 0603 | NTC Thermistor 10k 0603 (1608 Metric)
P19.1, X4 | S2B-ZR(LF)(SN) | 2 | "Batt Temp", T-DET | Connector Header Through Hole, Right Angle 2 position 0.059" (1.50mm)
P20, P28 | 0545500571 | 2 | S201, S202 | 5 Position FFC, FPC Connector Contacts, Top 0.020" (0.50mm) Surface Mount, Right Angle
P22 | S5B-ZR(LF)(SN) | 1 | BLDC I2C | Connector Header Through Hole, Right Angle 5 position 0.059" (1.50mm)
P24 | SMT-0440-S-R | 1 | BUZZ | Buzzers Transducer, Externally Driven 90mA 4kHz 70dB @ 3V, 10cm Surface Mount Solder Pads
P102 | 5025700893 | 1 | uSD Card | 10 (8 + 2) Position Card Connector Secure Digital - microSD™ Surface Mount, Right Angle Gold
Q1, Q9, Q12 | DMN32D2LV-7 | 3 | DMN32D2LV-7 | Mosfet Array 2 N-Channel (Dual) 30V 400mA 400mW Surface Mount SOT-563
Q2 | BSS816NWH6327XTSA1 | 1 | BSS816NWH6327XTSA1 | N-Channel 20V 1.4A (Ta) 500mW (Ta) Surface Mount PG-SOT323-3
Q3, Q4, Q5, Q6, Q7, Q8 | DTC143ZET1G | 6 | DTC143ZET1G | Pre-Biased Bipolar Transistor (BJT) NPN - Pre-Biased 50V 100mA 200mW Surface Mount SC-75, SOT-416
Q10, Q11, Q14 | BC847CW,115 | 3 | BC847CW,115 | Bipolar (BJT) Transistor NPN 45V 100mA 100MHz 200mW Surface Mount SOT-323-3
Q13 | EM6M2T2R | 1 | EM6M2T2R | Mosfet Array N and P-Channel 20V 200mA 150mW Surface Mount EMT6
R1, R4, R21, R24, R25, R26, R31, R37, R38, R42, R45, R55, R57, R60, R62, R63, R82, R85, R86, R87, R88, R108, R117, R120, R123, R124, R141, R142, R143, R151, R152, R153, R156, R157, R159, R161, R165 | RC0402FR-0710KP | 37 | RES SMD 10K OHM 1% 1/16W 0402 | 10 kOhms ±1% 0.063W, 1/16W Chip Resistor 0402 (1005 Metric) Moisture Resistant Thick Film
R2 | RC0402FR-0731K6L | 1 | RES SMD 31.6K OHM 1% 1/16W 0402 | 31.6 kOhms ±1% 0.063W, 1/16W Chip Resistor 0402 (1005 Metric) Moisture Resistant Thick Film
R3 | RC0402FR-075K36L | 1 | RES SMD 5.36K OHM 1% 1/16W 0402 | 5.36 kOhms ±1% 0.063W, 1/16W Chip Resistor 0402 (1005 Metric) Moisture Resistant Thick Film
R5, R6, R66, R67, R166 | RC0402FR-072K7L | 5 | RES SMD 2.7K OHM 1% 1/16W 0402 | 2.7 kOhms ±1% 0.063W, 1/16W Chip Resistor 0402 (1005 Metric) Moisture Resistant Thick Film
R7, R8, R9, R10, R11, R12, R13, R14, R15, R16, R17, R54, R56, R58, R68, R69, R97, R98, R114, R115, R135, R138 | RC0402FR-07100KL | 22 | RES SMD 100K OHM 1% 1/16W 0402 | 100 kOhms ±1% 0.063W, 1/16W Chip Resistor 0402 (1005 Metric) Moisture Resistant Thick Film
R18, R19, R22, R23, R29, R36, R39, R48, R49, R50, R51, R52, R61, R74, R75, R96, R100, R118, R121, R128, R129, R130, R131 | RC0402JR-070RL | 23 | RES SMD 0 OHM JUMPER 1/16W 0402, DNP* | 0 Ohms Jumper 0.063W, 1/16W Chip Resistor 0402 (1005 Metric) Moisture Resistant Thick Film
R20 | AC0402FR-0710RL | 1 | RES SMD 10 OHM 1% 1/16W 0402 | 10 Ohms ±1% 0.063W, 1/16W Chip Resistor 0402 (1005 Metric) Automotive AEC-Q200, Moisture Resistant Thick Film
R32, R33, R34, R35, R101, R104, R105, R106, R160 | RC0402FR-07402RL | 9 | RES SMD 402 OHM 1% 1/16W 0402 | 402 Ohms ±1% 0.063W, 1/16W Chip Resistor 0402 (1005 Metric) Moisture Resistant Thick Film
R43, R44, R46 | RC0402FR-072KL | 3 | RES SMD 2K OHM 1% 1/16W 0402 | 2 kOhms ±1% 0.063W, 1/16W Chip Resistor 0402 (1005 Metric) Moisture Resistant Thick Film
R47 | RC0402FR-0715KL | 1 | RES SMD 15K OHM 1% 1/16W 0402 | 15 kOhms ±1% 0.063W, 1/16W Chip Resistor 0402 (1005 Metric) Thick Film
R53 | RC0402FR-075K1L | 1 | RES SMD 5.1K OHM 1% 1/16W 0402 | 5.1 kOhms ±1% 0.063W, 1/16W Chip Resistor 0402 (1005 Metric) Moisture Resistant Thick Film
R59, R91, R92, R93, R94, R95, R132 | RC0402FR-07100RL | 7 | RES SMD 100 OHM 1% 1/16W 0402 | 100 Ohms ±1% 0.063W, 1/16W Chip Resistor 0402 (1005 Metric) Moisture Resistant Thick Film
R78 | RC0402FR-0768K1L | 1 | RES SMD 68.1K OHM 1% 1/16W 0402 | 68.1 kOhms ±1% 0.063W, 1/16W Chip Resistor 0402 (1005 Metric) Moisture Resistant Thick Film
R79, R80 | RC0402FR-0718K2L | 2 | RES SMD 18.2K OHM 1% 1/16W 0402 | 18.2 kOhms ±1% 0.063W, 1/16W Chip Resistor 0402 (1005 Metric) Moisture Resistant Thick Film
R81 | RC0402FR-07360KL | 1 | RES SMD 360KOHM 1% 1/16W 0402 | 360 kOhms ±1% 0.063W, 1/16W Chip Resistor 0402 (1005 Metric) Moisture Resistant Thick Film
R83, R109 | RC0402FR-071KL | 2 | RES SMD 1K OHM 1% 1/16W 0402 | 1 kOhms ±1% 0.063W, 1/16W Chip Resistor 0402 (1005 Metric) Moisture Resistant Thick Film
R84, R107 | RC0402FR-0747KL | 2 | RES SMD 47K OHM 1% 1/16W 0402 | 47 kOhms ±1% 0.063W, 1/16W Chip Resistor 0402 (1005 Metric) Moisture Resistant Thick Film
R89, R90 | CRCW25122R20JNEG | 2 | RES SMD 2.2 OHM 5% 1W 2512 | 2.2 Ohms ±5% 1W Chip Resistor 2512 (6432 Metric) Automotive AEC-Q200 Thick Film
R99 | RC0402FR-07536KL | 1 | RES SMD 536K OHM 1% 1/16W 0402 | 536 kOhms ±1% 0.063W, 1/16W Chip Resistor 0402 (1005 Metric) Moisture Resistant Thick Film
R102 | RC0402FR-0723K7L | 1 | RES SMD 23.7K OHM 1% 1/16W 0402 | 23.7 kOhms ±1% 0.063W, 1/16W Chip Resistor 0402 (1005 Metric) Moisture Resistant Thick Film
R103, R144 | YC248-JR-07100KL | 2 | RES ARRAY 8 RES 100K OHM 1606 | 100k Ohm ±5% 62.5mW Power Per Element Isolated Resistor Network/Array ±200ppm/°C 1606, Convex, Long Side Terminals
R112 | CRCW06032R26FKEA | 1 | RES SMD 2.26 OHM 1% 1/10W 0603 | 2.26 Ohms ±1% 0.1W, 1/10W Chip Resistor 0603 (1608 Metric) Automotive AEC-Q200 Thick Film
R125, R126, R127 | RC0402FR-072R2L | 3 | RES SMD 2.2 OHM 1% 1/16W 0402 | 2.2 Ohms ±1% 0.063W, 1/16W Chip Resistor 0402 (1005 Metric) Moisture Resistant Thick Film
R133, R134 | RC0402FR-07390KL | 2 | RES SMD 390K OHM 1% 1/16W 0402 | 390 kOhms ±1% 0.063W, 1/16W Chip Resistor 0402 (1005 Metric) Moisture Resistant Thick Film
R136, R137, R140 | RMCF0402FT75K0 | 3 | RES SMD 75K OHM 1% 1/16W 0402 | 75 kOhms ±1% 0.063W, 1/16W Chip Resistor 0402 (1005 Metric) Automotive AEC-Q200 Thick Film
R139 | RC0402FR-0727KL | 1 | RES SMD 27K OHM 1% 1/16W 0402 | 27 kOhms ±1% 0.063W, 1/16W Chip Resistor 0402 (1005 Metric) Moisture Resistant Thick Film
R145, R146, R147, R148, R149, R150, R154, R155 | RC0402FR-074K75P | 8 | RES SMD 4.75K OHM 1% 1/16W 0402 | 4.75 kOhms ±1% 0.063W, 1/16W Chip Resistor 0402 (1005 Metric) Moisture Resistant Thick Film
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

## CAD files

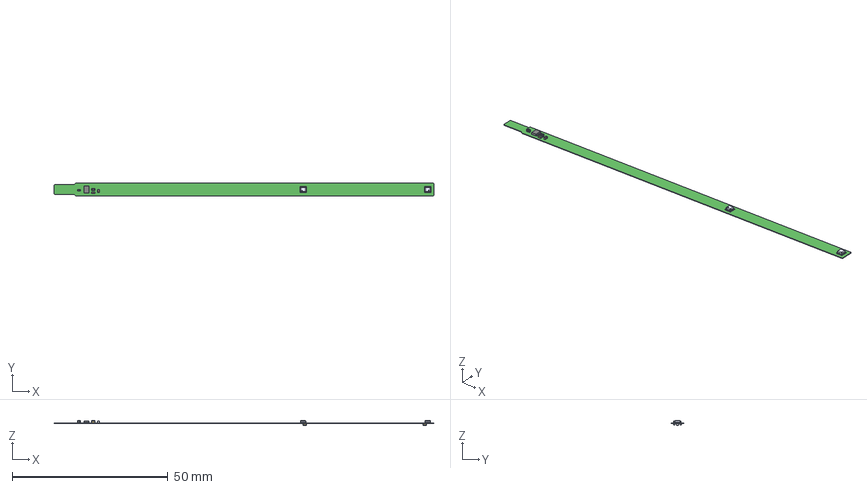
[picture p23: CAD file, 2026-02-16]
sensor-board-s201/hw-package/Assembly/Mechanical/20201207-SGU-Acme_CPU_Sensor_PCB_S201_001_3D_STEP_Flex.step
122.0 x 4.10 x 1.67 mm
BMP388--3DModel-STEP-56544 x 2
RC0402N x 4
DPV8_1P7X0P4
C0402C104Z4VACTU x 6

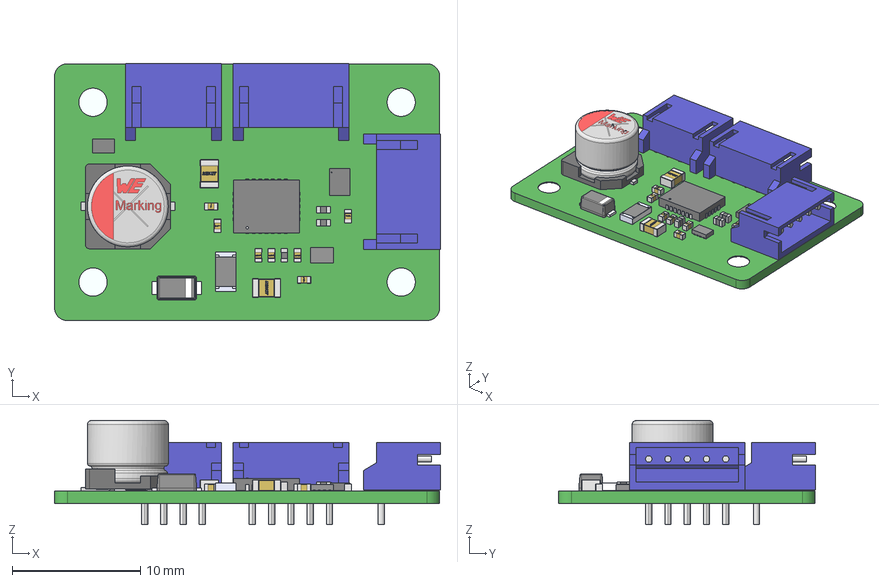
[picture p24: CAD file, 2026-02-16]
motor-driver-board-d201/hw-package/Assembly/Mechanical/20201105-VSI-Acme_CPU_Motor_Driver_D201_001_3D_STEP.step
30.1 x 20.0 x 8.10 mm
Board
RE1206FRE071ML
capicitor_6.3x5.5x2.2
Base_\X2\03A6\X0\6_3Capacitor
BODY-SON
PIN1-ID
DPV8_1P7X0P4
RHF24_2P65X3P65_TEX
RC0402N x 3
S5B-ZR x 2
S4B-ZR
SOD-123FL
C0402C104Z4VACTU x 7
C0805C101JAGACTU x 2
bigPin x 2

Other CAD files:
control-board-c201/hw-package/Assembly/Mechanical/No Variations/20201215-SGU-Acme_CPU_Control_Board_C201_001_DXF_Model.DXF
control_board_c202/hw-package/Assembly/Mechanical/No Variations/20201215-SGU-Acme_CPU_Control_Board_C201_001_DXF_Model.DXF
motor-driver-board-d201/hw-package/Assembly/Mechanical/20201105-VSI-Acme_CPU_Motor_Driver_D201_001_Plain_AutoCAD.DXF
sensor-board-s201/hw-package/Assembly/Mechanical/20201207-SGU-Acme_CPU_Sensor_PCB_S201_001_Plain_AutoCAD_Flex.DXF

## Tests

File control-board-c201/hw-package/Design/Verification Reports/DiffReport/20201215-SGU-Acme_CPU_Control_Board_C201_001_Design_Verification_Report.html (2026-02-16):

Altium

# Differences Report for Project Control_Board_Model_C201.PrjPcb and Control_Board_Model_C201_FFC_Sens_Conn.PcbDoc

Date: | | 12/22/2020
Time: | | 11:21:51 AM
Filename: | | G:\github-acme\Control_Board_Model_C_(HW_Package)\20201215\Design\Verification Reports\DiffReport\20201215-SGU-Acme_CPU_Control_Board_C201_001_Design_Verification_Report.html

## Extra Component Classes

Schematic Object | PCB Object
[P26]
[P31.2]

Back to top

## Extra Net Classes

Schematic Object | PCB Object
| [A1_[0..7]]
| [A2_[0..7]]
| [B1_[0..7]]
| [B2_[0..7]]

Back to top

## Component Classes With Extra Members

Schematic Object | PCB Object
[Q9]

Back to top

## Net Classes With Extra Members

Schematic Object | PCB Object
[B0_+1V8_VLT1]
[B1_+1V8_VLT1]
[B2_+1V8_VLT1]
[B3_+1V8_VLT1]
[B4_+1V8_VLT1]
[B4_+1V8_VLT1]
[B5_+1V8_VLT1]
[B5_+1V8_VLT1]
[B6_+1V8_VLT1]
[B6_+1V8_VLT1]
[B6_+1V8_VLT2]
[B7_+1V8_VLT1]
[B7_+1V8_VLT2]
[GPIO2]
[GPIO4]
[GPIO16]
[GPIO17]
[GPIO18]
[GPIO33]
[GPIO35]

Back to top

## Changed Net Names

Schematic Object | PCB Object
[A0_+1V8_VLT1] | [A1_0]
[A0_+1V8_VLT2] | [A2_0]
[A1_+1V8_VLT1] | [A1_1]
[A1_+1V8_VLT2] | [A2_1]
[A2_+1V8_VLT1] | [A1_2]
[A2_+1V8_VLT2] | [A2_2]
[A3_+1V8_VLT1] | [A1_3]
[A3_+1V8_VLT2] | [A2_3]
[A4_+1V8_VLT1] | [A1_4]
[A4_+1V8_VLT2] | [A2_4]
[A5_+1V8_VLT1] | [A1_5]
[A5_+1V8_VLT2] | [A2_5]
[A6_+1V8_VLT1] | [A1_6]
[A6_+1V8_VLT2] | [A2_6]
[A7_+1V8_VLT1] | [A1_7]
[A7_+1V8_VLT2] | [A2_7]
[B0_+1V8_VLT1] | [B1_0]
[B0_+1V8_VLT2] | [B2_0]
[B1_+1V8_VLT1] | [B1_1]
[B1_+1V8_VLT2] | [B2_1]
[B2_+1V8_VLT1] | [B1_2]
[B2_+1V8_VLT2] | [B2_2]
[B3_+1V8_VLT1] | [B1_3]
[B3_+1V8_VLT2] | [B2_3]
[B4_+1V8_VLT1] | [B1_4]
[B4_+1V8_VLT2] | [B2_4]
[B5_+1V8_VLT1] | [B1_5]
[B5_+1V8_VLT2] | [B2_5]
[B6_+1V8_VLT1] | [B1_6]
[B6_+1V8_VLT2] | [B2_6]
[B7_+1V8_VLT1] | [B1_7]
[B7_+1V8_VLT2] | [B2_7]
[PIN#6_P01] | [PIN#6_P012]

Back to top

## Changed Component Class Name

Schematic Object | PCB Object
[P01] | [P012]

Back to top

## Changed Rule

Schematic Object | PCB Object
[Width Constraint [Pref Impedance = 50.00ohms Min Impedance = 45.00ohms Max Impedance = 55.00ohms]] | [Width Constraint [Pref Width = 38.028mil Min Width = 4.007mil Max Width = 44.609mil]]
[Width Constraint [Pref Impedance = 50.00ohms Min Impedance = 45.00ohms Max Impedance = 55.00ohms]] | [Width Constraint [Pref Width = 38.028mil Min Width = 4.007mil Max Width = 44.609mil]]
[Width Constraint [Pref Impedance = 50.00ohms Min Impedance = 45.00ohms Max Impedance = 55.00ohms]] | [Width Constraint [Pref Width = 38.028mil Min Width = 4.007mil Max Width = 44.609mil]]
[Width Constraint [Pref Impedance = 50.00ohms Min Impedance = 45.00ohms Max Impedance = 55.00ohms]] | [Width Constraint [Pref Width = 38.028mil Min Width = 4.007mil Max Width = 44.609mil]]
[Width Constraint [Pref Impedance = 50.00ohms Min Impedance = 45.00ohms Max Impedance = 55.00ohms]] | [Width Constraint [Pref Width = 38.028mil Min Width = 4.007mil Max Width = 44.609mil]]

Back to top

## Different Component Parameters

Schematic Object | PCB Object
[Q9] | [Q9]

Back to top

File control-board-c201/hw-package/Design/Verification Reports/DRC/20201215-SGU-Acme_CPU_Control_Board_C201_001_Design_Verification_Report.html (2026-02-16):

Altium

# Design Rule Verification Report

Date: | | 12/22/2020
Time: | | 11:21:21 AM
Elapsed Time: | | 00:00:20
Filename: | | G:\github-acme\control-board-c201\control-board-c201\hardware-design\Control_Board_Model_C201_FFC_Sens_Conn.PcbDoc

Warnings: | | 0
Rule Violations: | | 0

## Summary

Warnings | Count
Total | 0

Rule Violations | Count
Clearance Constraint (Gap=6mil) (All),(All) | 0
Clearance Constraint (Gap=6mil) (OnLayer('4-SIG-HOR') or OnLayer('5-SIG-VERT')),(All) | 0
Short-Circuit Constraint (Allowed=No) (All),(All) | 0
Un-Routed Net Constraint ( (All) ) | 0
Modified Polygon (Allow modified: No), (Allow shelved: No) | 0
Width Constraint (Min=4.007mil) (Max=44.609mil) (Preferred=38.028mil) (InNet('NetC37_2')) | 0
Width Constraint (Min=6mil) (Max=200mil) (Preferred=10mil) (All) | 0
Width Constraint (Min=4.007mil) (Max=44.609mil) (Preferred=38.028mil) (InNet('NetC34_2')) | 0
Width Constraint (Min=4.007mil) (Max=44.609mil) (Preferred=38.028mil) (InNet('NetC33_2')) | 0
Width Constraint (Min=4.007mil) (Max=44.609mil) (Preferred=38.028mil) (InNet('NetC36_2')) | 0
Width Constraint (Min=4.007mil) (Max=44.609mil) (Preferred=38.028mil) (InNet('NetC35_2')) | 0
Routing Via (MinHoleWidth=5.906mil) (MaxHoleWidth=19.685mil) (PreferredHoleWidth=5.906mil) (MinWidth=19.685mil) (MaxWidth=27.559mil) (PreferedWidth=19.685mil) (All) | 0
Differential Pairs Uncoupled Length using the Gap Constraints (Min=6mil) (Max=6mil) (Prefered=6mil) and Width Constraints (Min=6mil) (Max=6mil) (Prefered=6mil) (All) | 0
Power Plane Connect Rule(Direct Connect )(Expansion=20mil) (Conductor Width=10mil) (Air Gap=10mil) (Entries=4) (IsVia) | 0
Power Plane Connect Rule(Relief Connect )(Expansion=6mil) (Conductor Width=6mil) (Air Gap=6mil) (Entries=4) (All) | 0
Minimum Annular Ring (Minimum=6mil) (All) | 0
Minimum Annular Ring (Minimum=0mil) (IsVia and not (OnTopLayer or OnBottomLayer)) | 0
Hole Size Constraint (Min=5.905mil) (Max=248.031mil) (All) | 0
Hole To Hole Clearance (Gap=10mil) (All),(All) | 0
Minimum Solder Mask Sliver (Gap=3mil) (All),(All) | 0
Silk To Solder Mask (Clearance=4mil) (IsPad),(All) | 0
Silk to Silk (Clearance=1mil) (All),(All) | 0
Net Antennae (Tolerance=0mil) (All) | 0
Board Clearance Constraint (Gap=0mil) (All) | 0
Board Clearance Constraint (Gap=0mil) (WithinRoom('PCB_Stackup')) | 0
Board Clearance Constraint (Gap=0mil) (WithinRoom('Layer_Names')) | 0
Board Clearance Constraint (Gap=0mil) (HasFootprintPad('MOLEX_2012670005','S3') or HasFootprintPad('MOLEX_2012670005','S4')) | 0
Board Clearance Constraint (Gap=0mil) (HasFootprintPad('5025700893','0')) | 0
Board Clearance Constraint (Gap=0mil) (HasFootprintPad('1042240820_MOL','G4') or HasFootprintPad('1042240820_MOL','G1') or ((ObjectKind = 'Fill') and HasFootprint('1042240820_MOL'))) | 0
Board Clearance Constraint (Gap=0mil) (OnBottomSilkscreen or OnTopSilkscreen) | 0
Matched Lengths(Tolerance=50mil) (InNetClass('QSPI')) | 0
Component Clearance Constraint ( Horizontal Gap = 0mil, Vertical Gap = 0mil ) (WithinRoom('PCB_Stackup')),(All) | 0
Component Clearance Constraint ( Horizontal Gap = 12mil, Vertical Gap = 40mil ) (All),(All) | 0
Component Clearance Constraint ( Horizontal Gap = 0mil, Vertical Gap = 0mil ) (HasFootprint('QG-2864KSWEG01_FLIPPED')),(HasFootprint('CONN_0524352271')) | 0
Component Clearance Constraint ( Horizontal Gap = 0mil, Vertical Gap = 0mil ) (HasFootprint('Net Tie 6x30mil')),(All) | 0
Component Clearance Constraint ( Horizontal Gap = 0mil, Vertical Gap = 0mil ) (HasFootprint('TC2030-IDC-NL') or HasFootprint('TC2050-IDC-NL')),(All) | 0
Height Constraint (Min=0mil) (Max=1000mil) (Prefered=500mil) (All) | 0
Total | 0

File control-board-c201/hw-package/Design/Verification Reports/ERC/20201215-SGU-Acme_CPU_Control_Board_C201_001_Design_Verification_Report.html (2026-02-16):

Altium

# Electrical Rule Check Report

Date: | | 12/22/2020
Time: | | 11:21:43 AM
Filename: | | G:\github-acme\Control_Board_Model_C_(HW_Package)\20201215\Design\Verification Reports\ERC\20201215-SGU-Acme_CPU_Control_Board_C201_001_Design_Verification_Report.html

Class | Document | Message
Error | Top_Control_Board_Model_C201.SchDoc | DIO_1_1 contains Output Sheet Entry and Bidirectional Sheet Entry objects (Sheet Entry P104-uSD_C_DET(Output), Sheet Entry IO-DIO_1_[0..15](I/O)).
Error | Top_Control_Board_Model_C201.SchDoc | DIO_1_5 contains Output Sheet Entry and Bidirectional Sheet Entry objects (Sheet Entry TLT_SENS-\INT1(Output), Sheet Entry IO-DIO_1_[0..15](I/O)).
Error | Logic_IO_Unit_V2.SchDoc | DIO_1_6 contains Bidirectional Port and Output Sheet Entry objects (Port DIO_1_[0..15], Sheet Entry 16xIO_2-\INT(Output)).
Error | Logic_IO_Unit_V2.SchDoc | DIO_1_6 contains Output Sheet Entry and Bidirectional Sheet Entry objects (Sheet Entry 16xIO_2-\INT(Output), Sheet Entry 16xIO_1-GPIO[0..15](I/O)).
Error | Top_Control_Board_Model_C201.SchDoc | DIO_1_14 contains Output Sheet Entry and Bidirectional Sheet Entry objects (Sheet Entry P16_P25-STP_DRV_FLT(Output), Sheet Entry IO-DIO_1_[0..15](I/O)).
Error | Top_Control_Board_Model_C201.SchDoc | DIO_2_1 contains Output Sheet Entry and Bidirectional Sheet Entry objects (Sheet Entry P109-STATUS(Output), Sheet Entry IO-DIO_2_[0..15](I/O)).
Error | Top_Control_Board_Model_C201.SchDoc | DIO_2_2 contains Output Sheet Entry and Bidirectional Sheet Entry objects (Sheet Entry P109-NET_STATUS(Output), Sheet Entry IO-DIO_2_[0..15](I/O)).
Error | Top_Control_Board_Model_C201.SchDoc | DIO_2_5 contains Output Sheet Entry and Bidirectional Sheet Entry objects (Sheet Entry P109-M_UART.RI(Output), Sheet Entry IO-DIO_2_[0..15](I/O)).
Error | Top_Control_Board_Model_C201.SchDoc | DIO_2_6 contains Output Sheet Entry and Bidirectional Sheet Entry objects (Sheet Entry P109-M_UART.DCD(Output), Sheet Entry IO-DIO_2_[0..15](I/O)).
Error | Top_Control_Board_Model_C201.SchDoc | DIO_2_7 contains Output Sheet Entry and Bidirectional Sheet Entry objects (Sheet Entry P109-PSM_IND(Output), Sheet Entry IO-DIO_2_[0..15](I/O)).
Error | Top_Control_Board_Model_C201.SchDoc | DIO_3_0 contains Output Sheet Entry and Bidirectional Sheet Entry objects (Sheet Entry TCPC-\TCPP_FLT(Output), Sheet Entry IO-DIO_3_[0..7](I/O)).
Error | Top_Control_Board_Model_C201.SchDoc | DIO_3_1 contains Output Sheet Entry and Bidirectional Sheet Entry objects (Sheet Entry TCPC-BC_CHG_DET(Output), Sheet Entry IO-DIO_3_[0..7](I/O)).
Error | Top_Control_Board_Model_C201.SchDoc | DIO_3_2 contains Output Sheet Entry and Bidirectional Sheet Entry objects (Sheet Entry TCPC-\BC_CHG__AL(Output), Sheet Entry IO-DIO_3_[0..7](I/O)).
Error | Top_Control_Board_Model_C201.SchDoc | DIO_3_5 contains Output Sheet Entry and Bidirectional Sheet Entry objects (Sheet Entry BC-\INT(Output), Sheet Entry IO-DIO_3_[0..7](I/O)).
Error | Top_Control_Board_Model_C201.SchDoc | DIO_3_7 contains Output Sheet Entry and Bidirectional Sheet Entry objects (Sheet Entry TCPC-USB_SW_OPN(Output), Sheet Entry IO-DIO_3_[0..7](I/O)).
Error | MCU_Module.SchDoc | PA0 contains Input Port and Bidirectional Sheet Entry objects (Port \UI_INT, Sheet Entry STM32G473CETx-PA[0..15](I/O)).
Error | MCU_Module.SchDoc | PA1 contains Output Port and Bidirectional Sheet Entry objects (Port SPEED_CTRL, Sheet Entry STM32G473CETx-PA[0..15](I/O)).
Error | MCU_Module.SchDoc | PA4 contains Output Port and Bidirectional Sheet Entry objects (Port FAN_PS_VREF, Sheet Entry STM32G473CETx-PA[0..15](I/O)).
Error | MCU_Module.SchDoc | PA5 contains Output Port and Bidirectional Sheet Entry objects (Port FRS_TX1, Sheet Entry STM32G473CETx-PA[0..15](I/O)).
Error | MCU_Module.SchDoc | PA8 contains Output Port and Bidirectional Sheet Entry objects (Port \IO_PE_RST, Sheet Entry STM32G473CETx-PA[0..15](I/O)).
Error | MCU_Module.SchDoc | PA15 contains Input Port and Bidirectional Sheet Entry objects (Port SPEED_SENSE, Sheet Entry STM32G473CETx-PA[0..15](I/O)).
Error | MCU_Module.SchDoc | PB2 contains Output Port and Bidirectional Sheet Entry objects (Port BUZZ, Sheet Entry STM32G473CETx-PB[0..15](I/O)).
Error | MCU_Module.SchDoc | PB9 contains Output Port and Bidirectional Sheet Entry objects (Port STP_CLK, Sheet Entry STM32G473CETx-PB[0..15](I/O)).
Error | MCU_Module.SchDoc | PB10 contains Input Port and Bidirectional Sheet Entry objects (Port BC_STAT, Sheet Entry STM32G473CETx-PB[0..15](I/O)).
Error | MCU_Module.SchDoc | PC0 contains Output Sheet Entry and Bidirectional Sheet Entry objects (Sheet Entry AN_IO-VFAN_ADC(Output), Sheet Entry STM32G473CETx-PC[0..15](I/O)).
Error | MCU_Module.SchDoc | PC1 contains Output Sheet Entry and Bidirectional Sheet Entry objects (Sheet Entry AN_IO-VBUS_ADC(Output), Sheet Entry STM32G473CETx-PC[0..15](I/O)).
Error | MCU_Module.SchDoc | PC2 contains Output Sheet Entry and Bidirectional Sheet Entry objects (Sheet Entry AN_IO-VBAT_ADC(Output), Sheet Entry STM32G473CETx-PC[0..15](I/O)).
Error | MCU_Module.SchDoc | PC3 contains Input Port and Bidirectional Sheet Entry objects (Port \SENSE_INT, Sheet Entry STM32G473CETx-PC[0..15](I/O)).
Error | MCU_Module.SchDoc | PC6 contains Output Port and Bidirectional Sheet Entry objects (Port LCD_BL_PWM, Sheet Entry STM32G473CETx-PC[0..15](I/O)).
Error | MCU_Module.SchDoc | PC7 contains Output Port and Bidirectional Sheet Entry objects (Port STP_VREF_PWM, Sheet Entry STM32G473CETx-PC[0..15](I/O)).
Error | MCU_Module.SchDoc | PC12 contains Output Port and Bidirectional Sheet Entry objects (Port FRS_TX2, Sheet Entry STM32G473CETx-PC[0..15](I/O)).
Error | MCU_Module.SchDoc | PC13 contains Input Port and Bidirectional Sheet Entry objects (Port TAMP_DET, Sheet Entry STM32G473CETx-PC[0..15](I/O)).
Warning | TXB0108 Voltage_Level_Translator.SchDoc | A0_+1V8_VLT1 contains Bidirectional Port and Unspecified Sheet Entry objects (Port A[0..7], Sheet Entry +1V8_VLT1-A[0..7](Passive)).
Warning | TXB0108 Voltage_Level_Translator.SchDoc | A0_+1V8_VLT2 contains Bidirectional Port and Unspecified Sheet Entry objects (Port A[0..7], Sheet Entry +1V8_VLT2-A[0..7](Passive)).
Warning | TXB0108 Voltage_Level_Translator.SchDoc | A1_+1V8_VLT1 contains Bidirectional Port and Unspecified Sheet Entry objects (Port A[0..7], Sheet Entry +1V8_VLT1-A[0..7](Passive)).
Warning | TXB0108 Voltage_Level_Translator.SchDoc | A1_+1V8_VLT2 contains Bidirectional Port and Unspecified Sheet Entry objects (Port A[0..7], Sheet Entry +1V8_VLT2-A[0..7](Passive)).
Warning | TXB0108 Voltage_Level_Translator.SchDoc | A2_+1V8_VLT1 contains Bidirectional Port and Unspecified Sheet Entry objects (Port A[0..7], Sheet Entry +1V8_VLT1-A[0..7](Passive)).
Warning | TXB0108 Voltage_Level_Translator.SchDoc | A2_+1V8_VLT2 contains Bidirectional Port and Unspecified Sheet Entry objects (Port A[0..7], Sheet Entry +1V8_VLT2-A[0..7](Passive)).
Warning | TXB0108 Voltage_Level_Translator.SchDoc | A3_+1V8_VLT1 contains Bidirectional Port and Unspecified Sheet Entry objects (Port A[0..7], Sheet Entry +1V8_VLT1-A[0..7](Passive)).
Warning | TXB0108 Voltage_Level_Translator.SchDoc | A3_+1V8_VLT2 contains Bidirectional Port and Unspecified Sheet Entry objects (Port A[0..7], Sheet Entry +1V8_VLT2-A[0..7](Passive)).
Warning | TXB0108 Voltage_Level_Translator.SchDoc | A4_+1V8_VLT1 contains Bidirectional Port and Unspecified Sheet Entry objects (Port A[0..7], Sheet Entry +1V8_VLT1-A[0..7](Passive)).
Warning | TXB0108 Voltage_Level_Translator.SchDoc | A4_+1V8_VLT2 contains Bidirectional Port and Unspecified Sheet Entry objects (Port A[0..7], Sheet Entry +1V8_VLT2-A[0..7](Passive)).
Warning | TXB0108 Voltage_Level_Translator.SchDoc | A5_+1V8_VLT1 contains Bidirectional Port and Unspecified Sheet Entry objects (Port A[0..7], Sheet Entry +1V8_VLT1-A[0..7](Passive)).
Warning | TXB0108 Voltage_Level_Translator.SchDoc | A5_+1V8_VLT2 contains Bidirectional Port and Unspecified Sheet Entry objects (Port A[0..7], Sheet Entry +1V8_VLT2-A[0..7](Passive)).
Warning | TXB0108 Voltage_Level_Translator.SchDoc | A6_+1V8_VLT1 contains Bidirectional Port and Unspecified Sheet Entry objects (Port A[0..7], Sheet Entry +1V8_VLT1-A[0..7](Passive)).
Warning | TXB0108 Voltage_Level_Translator.SchDoc | A6_+1V8_VLT2 contains Bidirectional Port and Unspecified Sheet Entry objects (Port A[0..7], Sheet Entry +1V8_VLT2-A[0..7](Passive)).
Warning | TXB0108 Voltage_Level_Translator.SchDoc | A7_+1V8_VLT1 contains Bidirectional Port and Unspecified Sheet Entry objects (Port A[0..7], Sheet Entry +1V8_VLT1-A[0..7](Passive)).
Warning | TXB0108 Voltage_Level_Translator.SchDoc | A7_+1V8_VLT2 contains Bidirectional Port and Unspecified Sheet Entry objects (Port A[0..7], Sheet Entry +1V8_VLT2-A[0..7](Passive)).
Warning | Sensor Connection.SchDoc | Adding items to hidden net GND
Warning | TXB0108 Voltage_Level_Translator.SchDoc | B0_+1V8_VLT1 contains Bidirectional Port and Unspecified Sheet Entry objects (Port B[0..7], Sheet Entry +1V8_VLT1-B[0..7](Passive)).
Warning | TXB0108 Voltage_Level_Translator.SchDoc | B0_+1V8_VLT2 contains Bidirectional Port and Unspecified Sheet Entry objects (Port B[0..7], Sheet Entry +1V8_VLT2-B[0..7](Passive)).
Warning | TXB0108 Voltage_Level_Translator.SchDoc | B1_+1V8_VLT1 contains Bidirectional Port and Unspecified Sheet Entry objects (Port B[0..7], Sheet Entry +1V8_VLT1-B[0..7](Passive)).
Warning | TXB0108 Voltage_Level_Translator.SchDoc | B1_+1V8_VLT2 contains Bidirectional Port and Unspecified Sheet Entry objects (Port B[0..7], Sheet Entry +1V8_VLT2-B[0..7](Passive)).
Warning | TXB0108 Voltage_Level_Translator.SchDoc | B2_+1V8_VLT1 contains Bidirectional Port and Unspecified Sheet Entry objects (Port B[0..7], Sheet Entry +1V8_VLT1-B[0..7](Passive)).
Warning | TXB0108 Voltage_Level_Translator.SchDoc | B2_+1V8_VLT2 contains Bidirectional Port and Unspecified Sheet Entry objects (Port B[0..7], Sheet Entry +1V8_VLT2-B[0..7](Passive)).
Warning | TXB0108 Voltage_Level_Translator.SchDoc | B3_+1V8_VLT1 contains Bidirectional Port and Unspecified Sheet Entry objects (Port B[0..7], Sheet Entry +1V8_VLT1-B[0..7](Passive)).
Warning | TXB0108 Voltage_Level_Translator.SchDoc | B3_+1V8_VLT2 contains Bidirectional Port and Unspecified Sheet Entry objects (Port B[0..7], Sheet Entry +1V8_VLT2-B[0..7](Passive)).
Warning | TXB0108 Voltage_Level_Translator.SchDoc | B4_+1V8_VLT1 contains Bidirectional Port and Unspecified Sheet Entry objects (Port B[0..7], Sheet Entry +1V8_VLT1-B[0..7](Passive)).
Warning | TXB0108 Voltage_Level_Translator.SchDoc | B4_+1V8_VLT2 contains Bidirectional Port and Unspecified Sheet Entry objects (Port B[0..7], Sheet Entry +1V8_VLT2-B[0..7](Passive)).
Warning | TXB0108 Voltage_Level_Translator.SchDoc | B5_+1V8_VLT1 contains Bidirectional Port and Unspecified Sheet Entry objects (Port B[0..7], Sheet Entry +1V8_VLT1-B[0..7](Passive)).
Warning | TXB0108 Voltage_Level_Translator.SchDoc | B5_+1V8_VLT2 contains Bidirectional Port and Unspecified Sheet Entry objects (Port B[0..7], Sheet Entry +1V8_VLT2-B[0..7](Passive)).
Warning | TXB0108 Voltage_Level_Translator.SchDoc | B6_+1V8_VLT1 contains Bidirectional Port and Unspecified Sheet Entry objects (Port B[0..7], Sheet Entry +1V8_VLT1-B[0..7](Passive)).
Warning | TXB0108 Voltage_Level_Translator.SchDoc | B6_+1V8_VLT2 contains Bidirectional Port and Unspecified Sheet Entry objects (Port B[0..7], Sheet Entry +1V8_VLT2-B[0..7](Passive)).
Warning | TXB0108 Voltage_Level_Translator.SchDoc | B7_+1V8_VLT1 contains Bidirectional Port and Unspecified Sheet Entry objects (Port B[0..7], Sheet Entry +1V8_VLT1-B[0..7](Passive)).
Warning | TXB0108 Voltage_Level_Translator.SchDoc | B7_+1V8_VLT2 contains Bidirectional Port and Unspecified Sheet Entry objects (Port B[0..7], Sheet Entry +1V8_VLT2-B[0..7](Passive)).
Warning | ESP32-WROOM32D_Module.SchDoc | GPIO0 contains IO Pin and Unspecified Port objects (Pin ESP32_MOD-25, Port GPIO[0..19]).
Warning | ESP32-WROOM32D_Module.SchDoc | GPIO1 contains Output Pin and Unspecified Port objects (Pin ESP32_MOD-35, Port GPIO[0..19]).
Warning | ESP32_Module.SchDoc | GPIO2 contains Input Port and Unspecified Sheet Entry objects (Port \SENS_INT, Sheet Entry U_ESP32-WROOM32D_Module-GPIO[0..19](Passive)).
Warning | ESP32-WROOM32D_Module.SchDoc | GPIO2 contains IO Pin and Unspecified Port objects (Pin ESP32_MOD-24, Port GPIO[0..19]).
Warning | ESP32-WROOM32D_Module.SchDoc | GPIO3 contains Input Pin and Unspecified Port objects (Pin ESP32_MOD-34, Port GPIO[0..19]).
Warning | ESP32-WROOM32D_Module.SchDoc | GPIO4 contains IO Pin and Unspecified Port objects (Pin ESP32_MOD-26, Port GPIO[0..19]).
Warning | ESP32_Module.SchDoc | GPIO5 contains Input Port and Unspecified Sheet Entry objects (Port \PERIPH_INT, Sheet Entry U_ESP32-WROOM32D_Module-GPIO[0..19](Passive)).
Warning | ESP32-WROOM32D_Module.SchDoc | GPIO5 contains IO Pin and Unspecified Port objects (Pin ESP32_MOD-29, Port GPIO[0..19]).
Warning | ESP32-WROOM32D_Module.SchDoc | GPIO6 contains IO Pin and Unspecified Port objects (Pin ESP32_MOD-20, Port GPIO[0..19]).
Warning | ESP32-WROOM32D_Module.SchDoc | GPIO7 contains IO Pin and Unspecified Port objects (Pin ESP32_MOD-21, Port GPIO[0..19]).
Warning | ESP32-WROOM32D_Module.SchDoc | GPIO8 contains IO Pin and Unspecified Port objects (Pin ESP32_MOD-22, Port GPIO[0..19]).
Warning | ESP32-WROOM32D_Module.SchDoc | GPIO9 contains IO Pin and Unspecified Port objects (Pin ESP32_MOD-17, Port GPIO[0..19]).
Warning | ESP32-WROOM32D_Module.SchDoc | GPIO10 contains IO Pin and Unspecified Port objects (Pin ESP32_MOD-18, Port GPIO[0..19]).
Warning | ESP32-WROOM32D_Module.SchDoc | GPIO11 contains IO Pin and Unspecified Port objects (Pin ESP32_MOD-19, Port GPIO[0..19]).
Warning | ESP32-WROOM32D_Module.SchDoc | GPIO12 contains IO Pin and Unspecified Port objects (Pin ESP32_MOD-14, Port GPIO[0..19]).
Warning | ESP32-WROOM32D_Module.SchDoc | GPIO13 contains IO Pin and Unspecified Port objects (Pin ESP32_MOD-16, Port GPIO[0..19]).
Warning | ESP32-WROOM32D_Module.SchDoc | GPIO14 contains IO Pin and Unspecified Port objects (Pin ESP32_MOD-13, Port GPIO[0..19]).
Warning | ESP32-WROOM32D_Module.SchDoc | GPIO15 contains IO Pin and Unspecified Port objects (Pin ESP32_MOD-23, Port GPIO[0..19]).
Warning | ESP32-WROOM32D_Module.SchDoc | GPIO16 contains IO Pin and Unspecified Port objects (Pin ESP32_MOD-27, Port GPIO[0..19]).
Warning | ESP32-WROOM32D_Module.SchDoc | GPIO17 contains IO Pin and Unspecified Port objects (Pin ESP32_MOD-28, Port GPIO[0..19]).
Warning | ESP32-WROOM32D_Module.SchDoc | GPIO18 contains IO Pin and Unspecified Port objects (Pin ESP32_MOD-30, Port GPIO[0..19]).
Warning | ESP32-WROOM32D_Module.SchDoc | GPIO19 contains IO Pin and Unspecified Port objects (Pin ESP32_MOD-31, Port GPIO[0..19]).
Warning | ESP32-WROOM32D_Module.SchDoc | GPIO21 contains IO Pin and Unspecified Port objects (Pin ESP32_MOD-33, Port GPIO[21..23]).
Warning | ESP32-WROOM32D_Module.SchDoc | GPIO22 contains IO Pin and Unspecified Port objects (Pin ESP32_MOD-36, Port GPIO[21..23]).
Warning | ESP32-WROOM32D_Module.SchDoc | GPIO23 contains IO Pin and Unspecified Port objects (Pin ESP32_MOD-37, Port GPIO[21..23]).
Warning | ESP32_Module.SchDoc | GPIO25 contains Bidirectional Port and Unspecified Sheet Entry objects (Port UART1.DTR, Sheet Entry U_ESP32-WROOM32D_Module-GPIO[25..27](Passive)).
Warning | ESP32-WROOM32D_Module.SchDoc | GPIO25 contains IO Pin and Unspecified Port objects (Pin ESP32_MOD-10, Port GPIO[25..27]).
Warning | ESP32-WROOM32D_Module.SchDoc | GPIO26 contains IO Pin and Unspecified Port objects (Pin ESP32_MOD-11, Port GPIO[25..27]).
Warning | ESP32-WROOM32D_Module.SchDoc | GPIO27 contains IO Pin and Unspecified Port objects (Pin ESP32_MOD-12, Port GPIO[25..27]).
Warning | ESP32-WROOM32D_Module.SchDoc | GPIO32 contains IO Pin and Unspecified Port objects (Pin ESP32_MOD-8, Port GPIO[32..33]).
Warning | ESP32-WROOM32D_Module.SchDoc | GPIO33 contains IO Pin and Unspecified Port objects (Pin ESP32_MOD-9, Port GPIO[32..33]).
Warning | BMA253_Triaxial_Acceleration_Sensor.SchDoc | NetNT4_1 contains Output Port and Unspecified Sheet Entry objects (Port SDO/SA0, Sheet Entry P128-SDO/SA0(Passive)).
Warning | MCU_Module.SchDoc | PC14 contains Bidirectional Sheet Entry and Unspecified Sheet Entry objects (Sheet Entry STM32G473CETx-PC[0..15](I/O), Sheet Entry RTC_XTAL-OSC32_IN(Passive)).
Warning | MCU_Module.SchDoc | PC15 contains Bidirectional Sheet Entry and Unspecified Sheet Entry objects (Sheet Entry STM32G473CETx-PC[0..15](I/O), Sheet Entry RTC_XTAL-OSC32_OUT(Passive)).

Back to top

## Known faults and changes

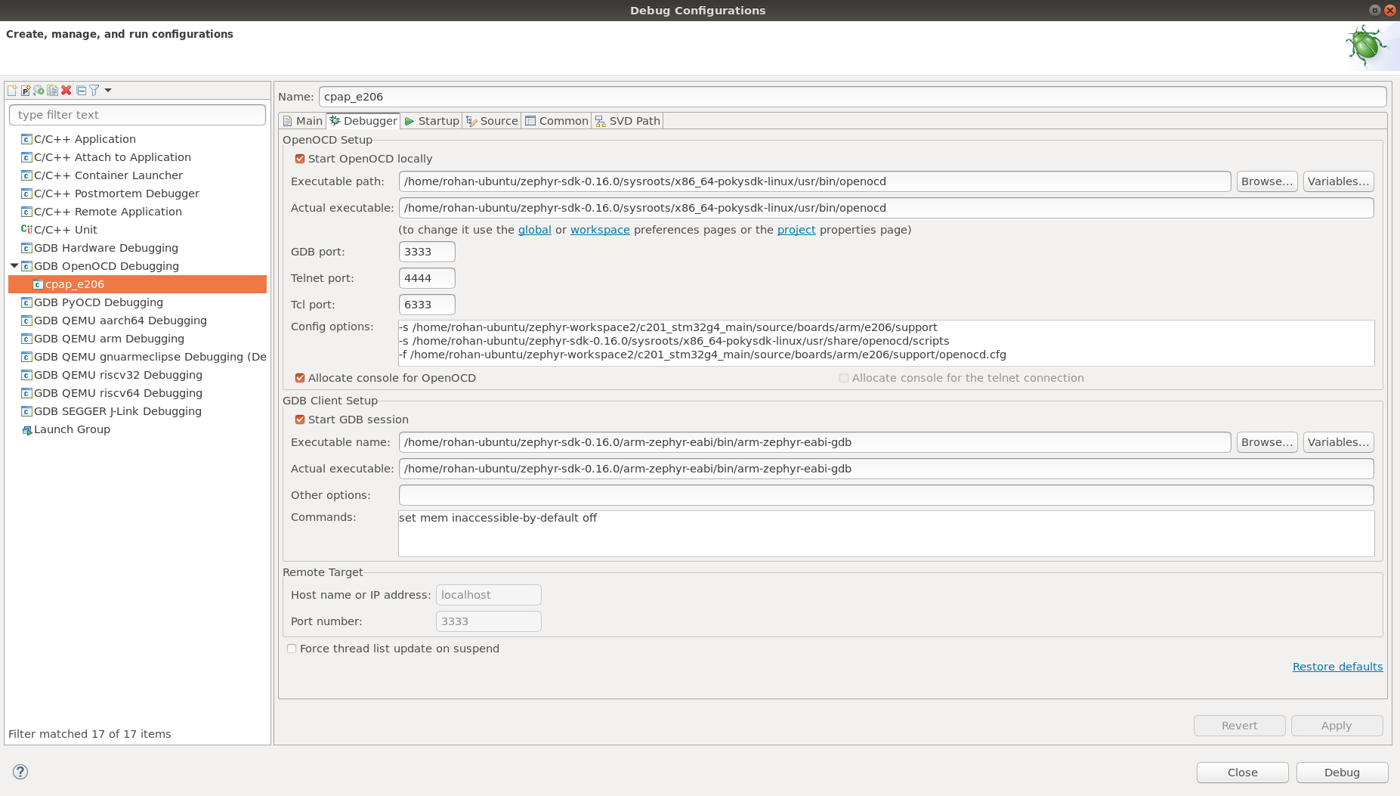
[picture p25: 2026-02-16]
firmware_general/openocd/openocd_eclipse_debugger.png

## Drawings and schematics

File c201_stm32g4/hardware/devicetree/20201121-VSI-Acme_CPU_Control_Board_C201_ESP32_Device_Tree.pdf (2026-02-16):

# Control Board Model C201

# ESP32 SOM Device Tree

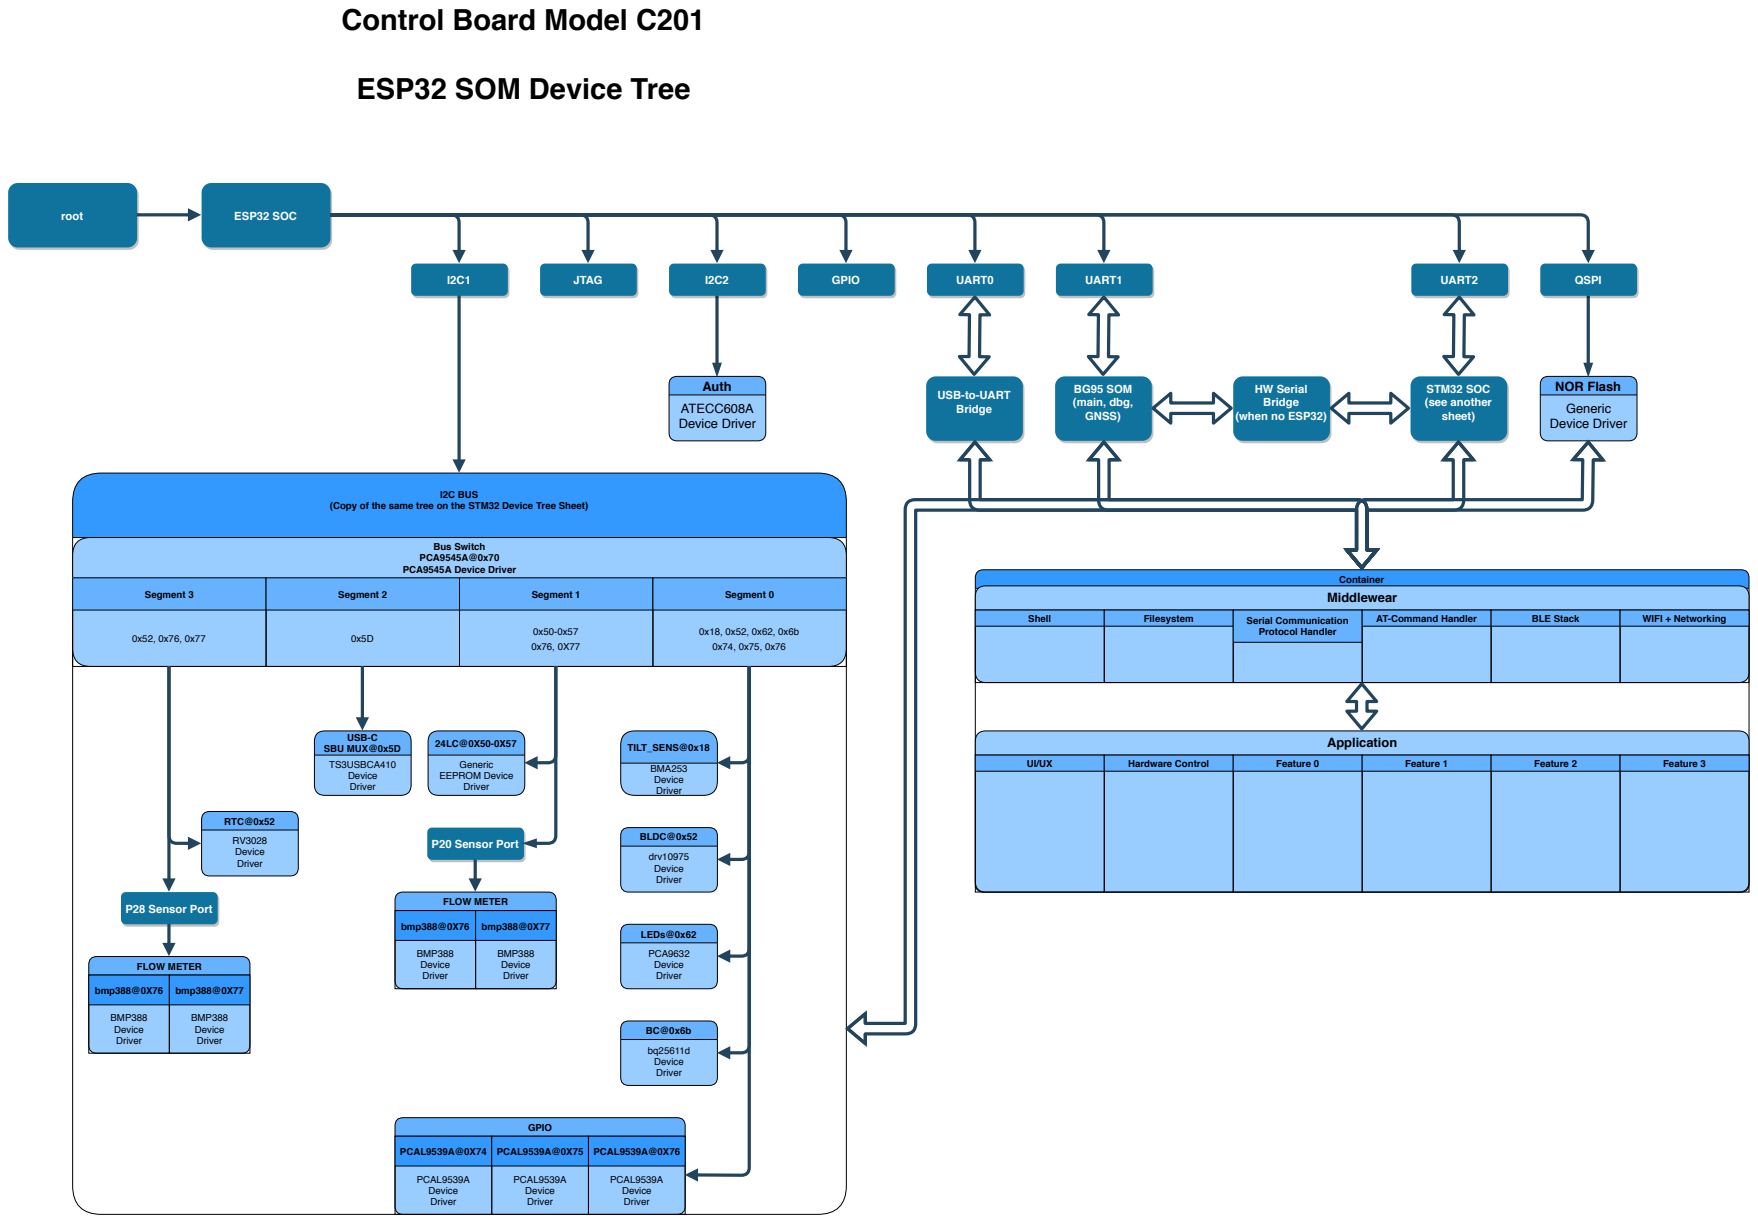
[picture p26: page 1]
root; ESP32 SOC; JTAG; GPIO; UART1; UART2; STM32 SOC (see another sheet); BG95 SOM (main, dbg, GNSS); UART0; I2C BUS; Bus Switch PCA9545A@0x70 PCA9545A Device Driver; Segment 3; Segment 2; Segment 1; Segment 0; P28 Sensor Port; bq25611d Device Driver; BLDC@0x52; drv10975 Device Driver; LEDs@0x62; PCA9632 Device Driver; TILT_SENS@0x18; BMA253 Device Driver; Generic EEPROM Device Driver; FLOW METER; USB-C SBU MUX@0x5D; TS3USBCA410 Device Driver; P20 Sensor Port; RTC@0x52; RV3028 Device Driver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

USB-to-UART
Bridge

(Copy of the same tree on the STM32 Device Tree Sheet)

bmp388@0X76 | bmp388@0X77

BMP388 Device Driver | BMP388 Device Driver

PCAL9539A@0X74 | PCAL9539A@0X75 | PCAL9539A@0X76

PCAL9539A Device Driver | PCAL9539A Device Driver | PCAL9539A Device Driver

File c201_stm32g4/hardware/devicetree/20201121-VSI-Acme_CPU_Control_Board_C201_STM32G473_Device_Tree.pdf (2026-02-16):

# Control Board Model C201

# STM32G473 SOC Device Tree

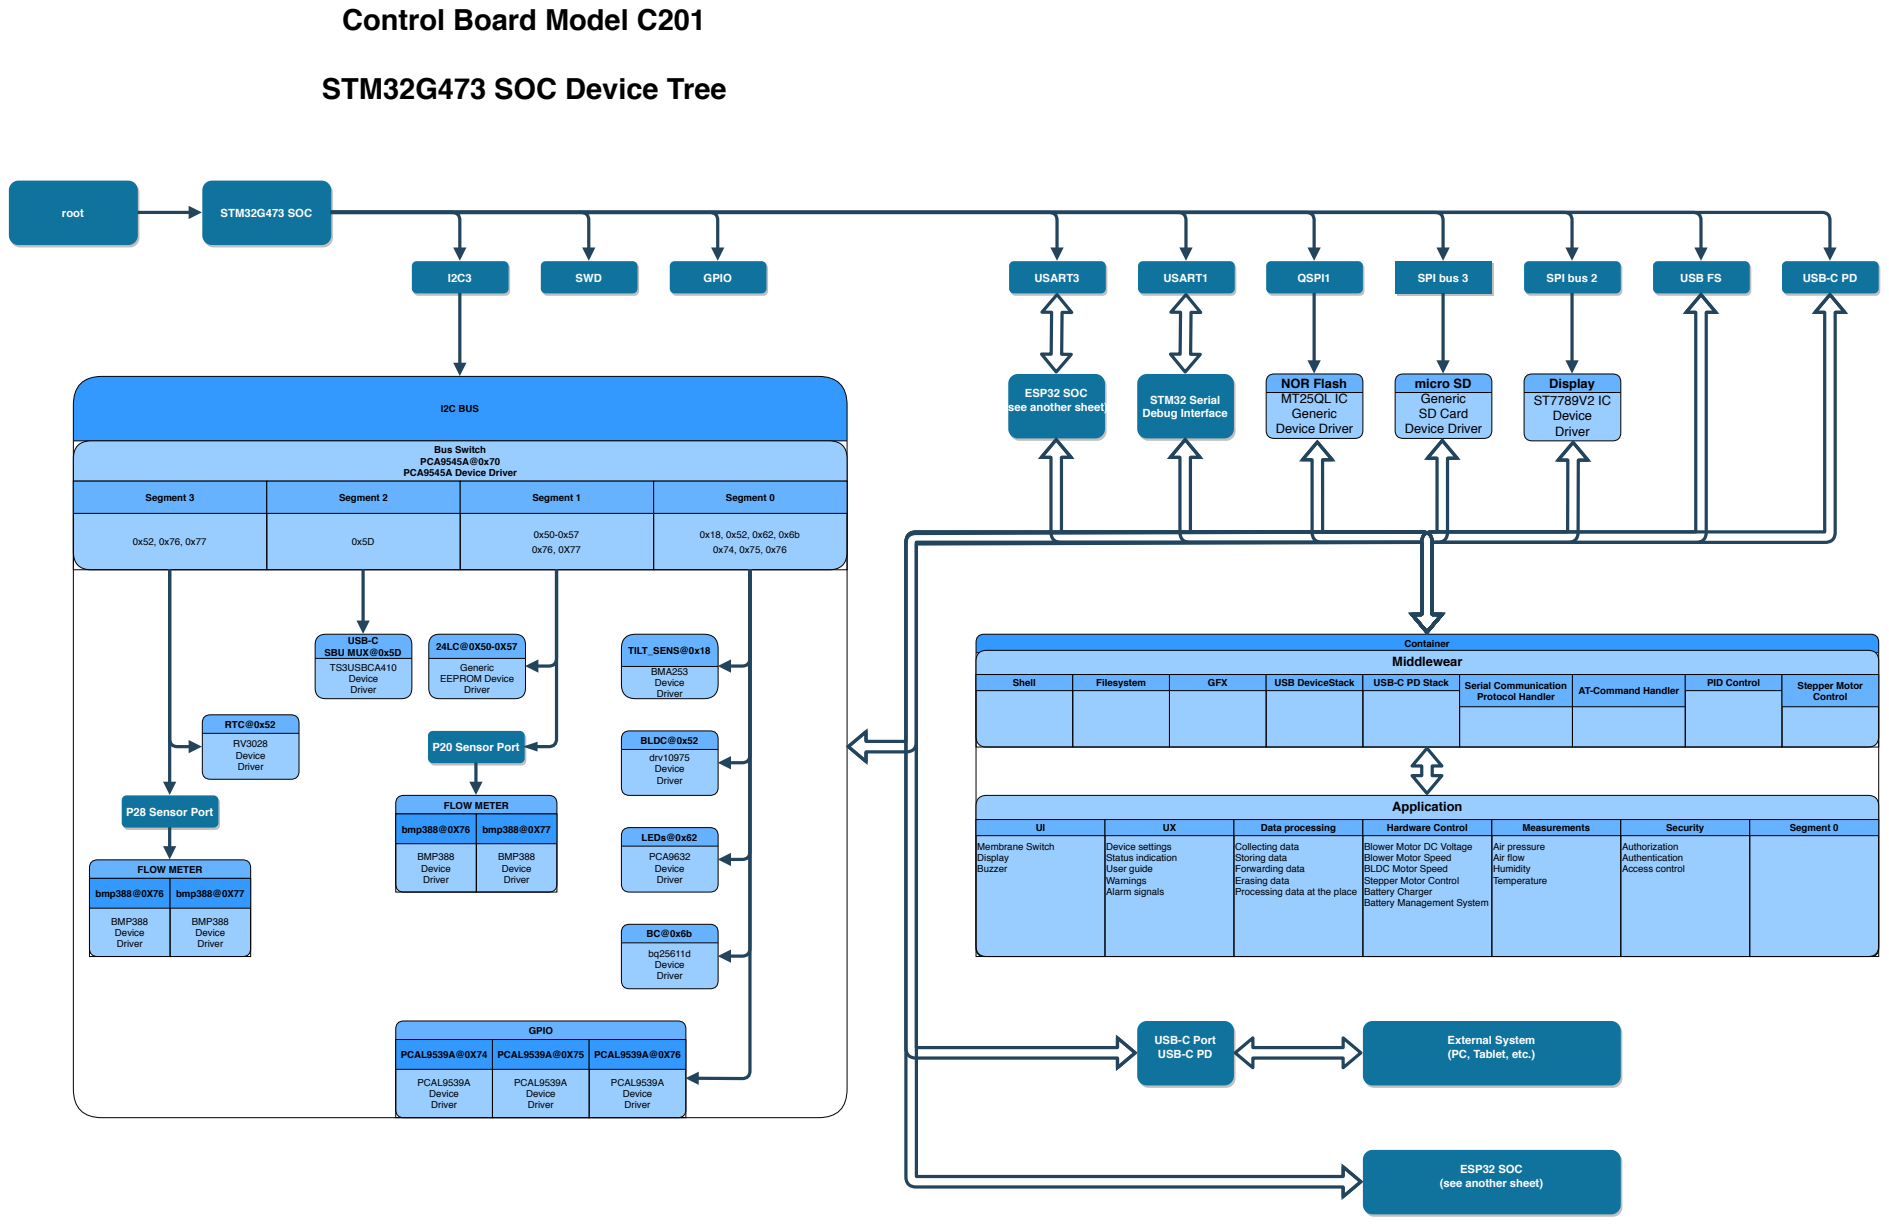
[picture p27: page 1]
root; STM32G473 SOC; QSPI1; SPI bus 3; USART3; USART1; SPI bus 2; Display ST7789V2 IC Device Driver; micro SD Generic SD Card Device Driver; NOR Flash MT25QL IC Generic Device Driver; STM32 Serial Debug Interface; SWD; GPIO; USB FS; USB-C PD; Container Middlewear; Shell; Filesystem; GFX; USB DeviceStack; USB-C PD Stack; Serial Communication; Protocol Handler; AT-Command Handler; PID Control; Stepper Motor; Control; Application; I2C BUS; Bus Switch PCA9545A@0x70 PCA9545A Device Driver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

ESP32 SOC
(see another sheet)

Segment 3 | Segment 2 | Segment 1 | Segment 0

bmp388@0X76 | bmp388@0X77

UI | UX | Data processing | Hardware Control | Measurements | Security | Segment 0

Membrane Switch Display Buzzer | Device settings Status indication User guide Warnings Alarm signals | Collecting data Storing data Forwarding data Erasing data Processing data at the place | Blower Motor DC Voltage Blower Motor Speed BLDC Motor Speed Stepper Motor Control Battery Charger Battery Management System | Air pressure Air flow Humidity Temperature | Authorization Authentication Access control

BMP388 Device Driver | BMP388 Device Driver

External System
(PC, Tablet, etc.)

PCAL9539A@0X74 | PCAL9539A@0X75 | PCAL9539A@0X76

PCAL9539A Device Driver | PCAL9539A Device Driver | PCAL9539A Device Driver

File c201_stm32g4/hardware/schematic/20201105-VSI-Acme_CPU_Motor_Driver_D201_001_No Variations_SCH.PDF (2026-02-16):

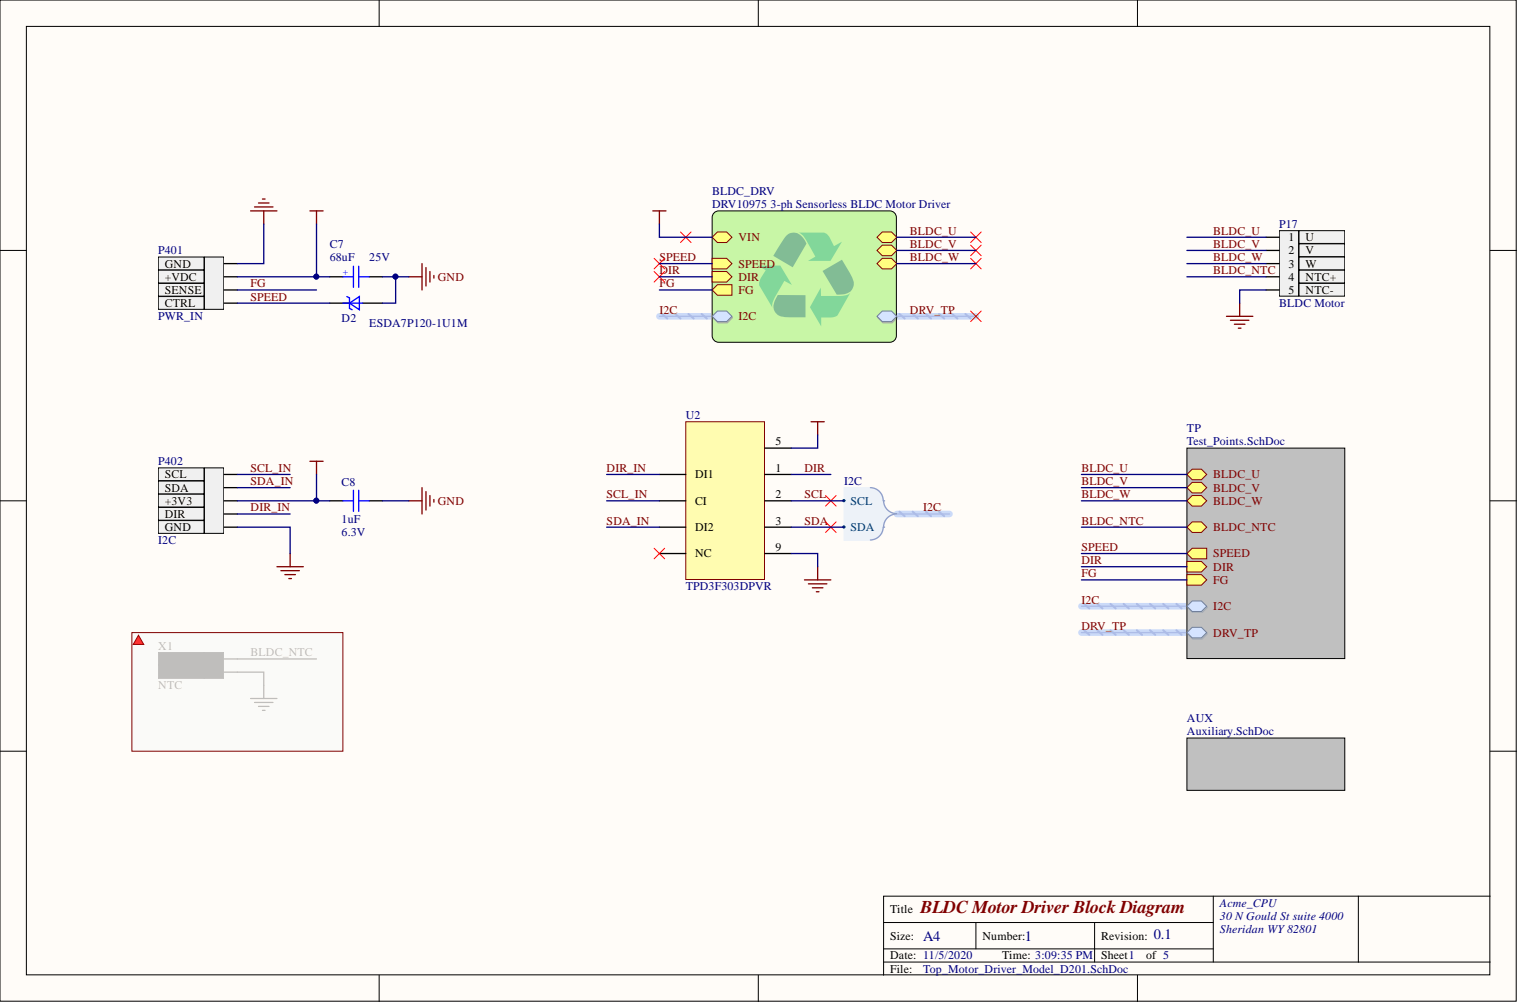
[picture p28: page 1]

BLDC Motor Driver Block Diagra m T i t l e | Acme_CP U 3 0 N G o u l d S t s u i te 4 0 0 0 S her i d a n WY 8

Size: A | N umber: | Rev i s i o n :
Date: / / T ime: : : 5 PM | | Sheet o f

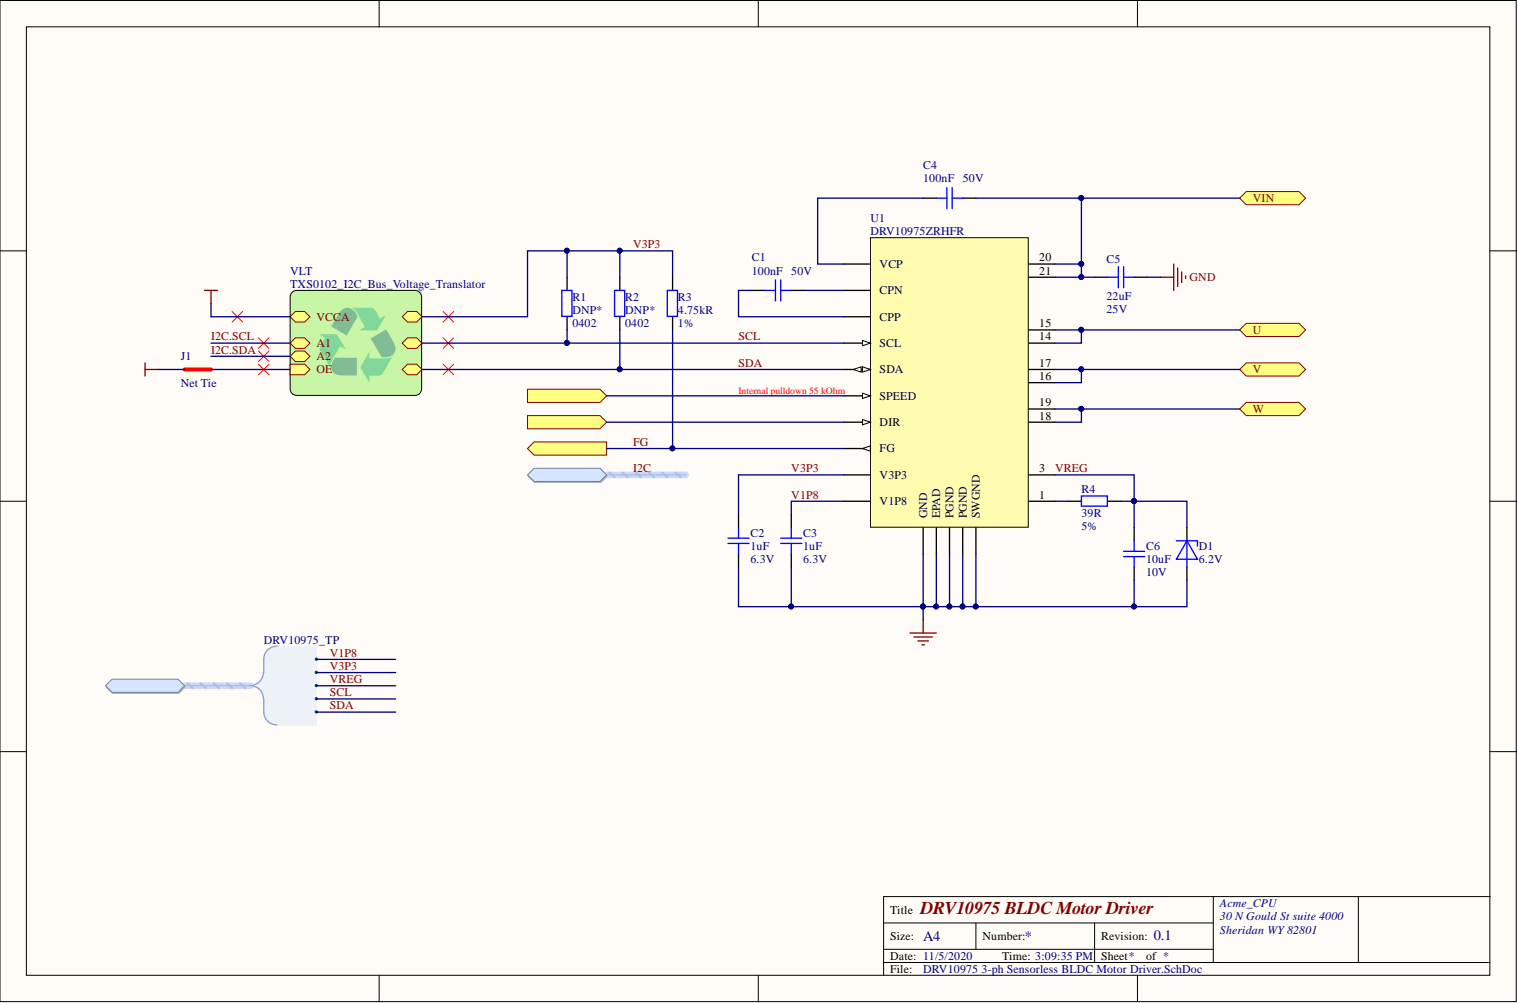
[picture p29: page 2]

DRV10975 BLDC Motor Driver Title | Acme_CPU 30 N Gould St suite 4000 Sheridan WY 82801

Size: A4 | Number: | Revision:
11/5/2020 Time: 3:09:35 PM | | Sheet * of *

DRV10975 3-ph Sensorless BLDC Motor Driver.SchDoc

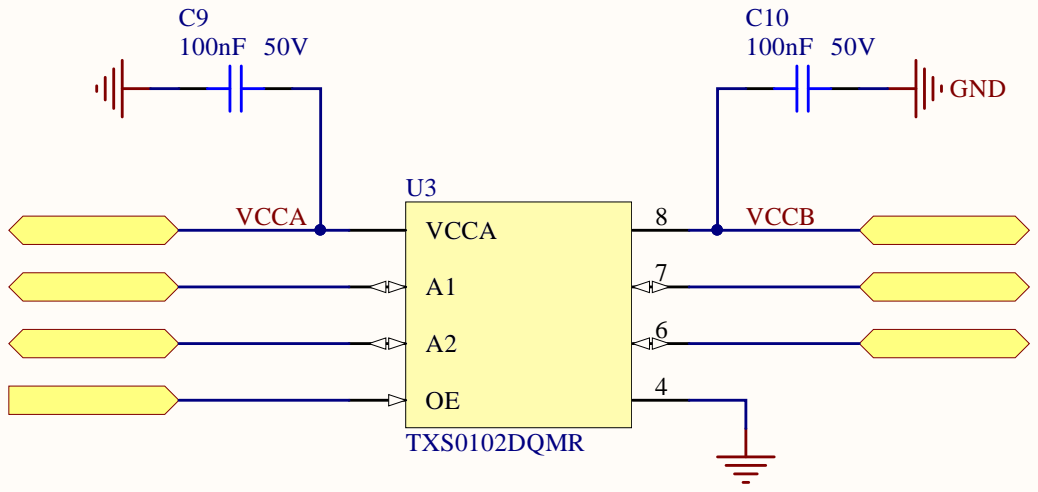
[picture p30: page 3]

I2C Bus Buffer - Voltage Translator
Title

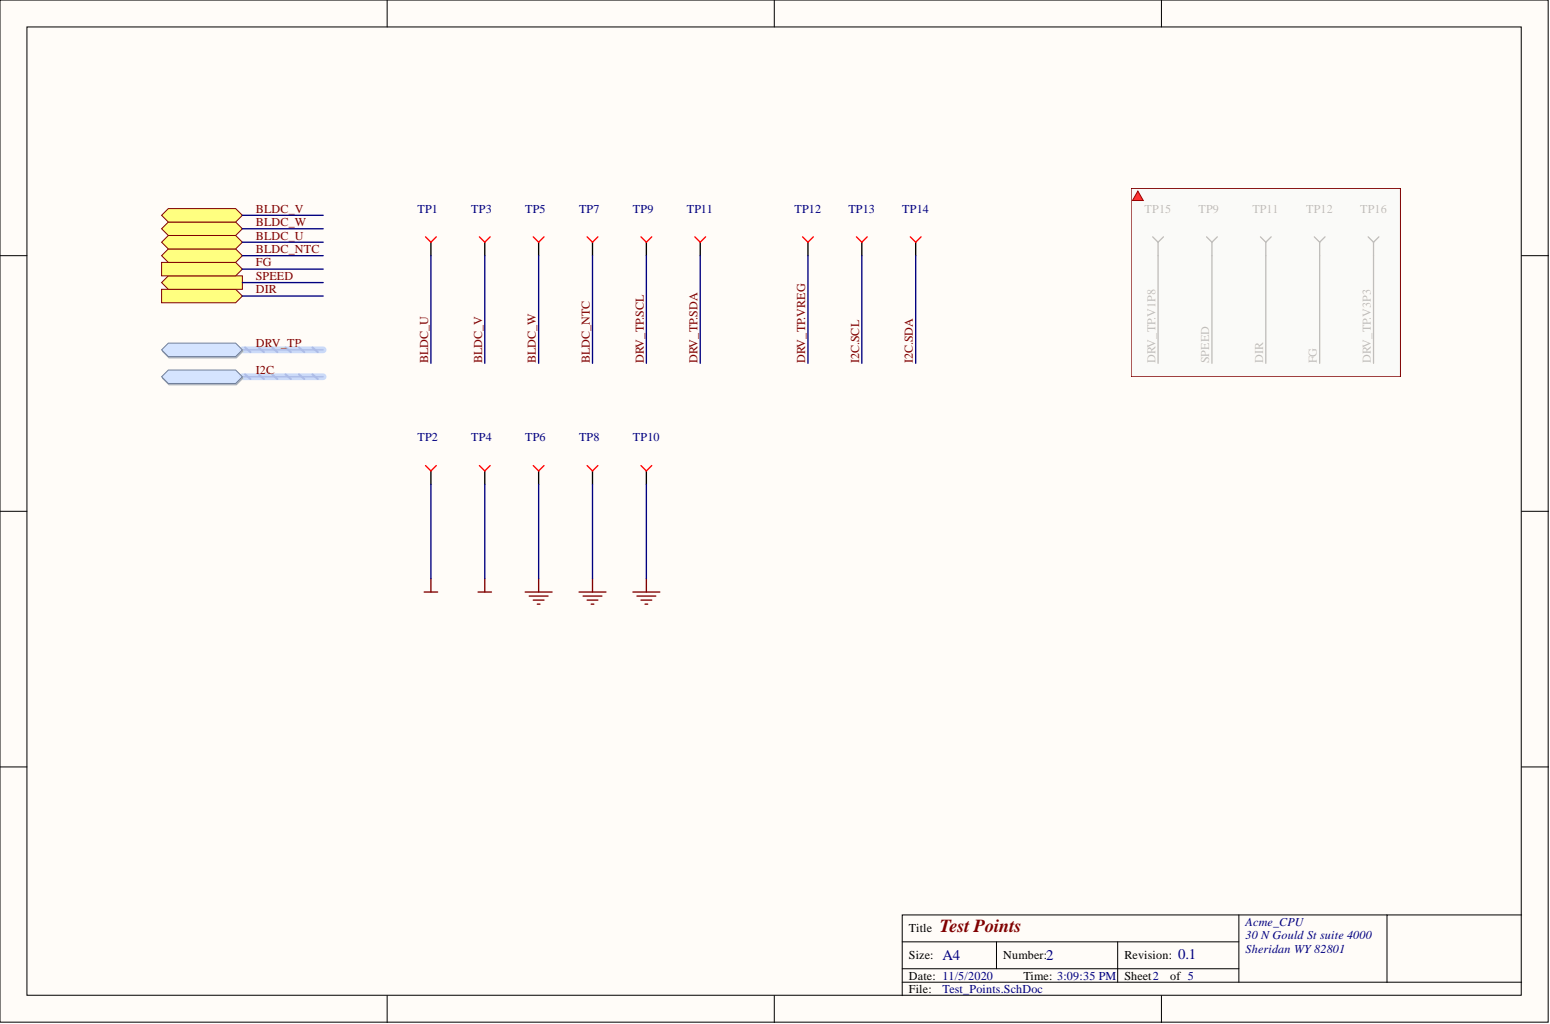
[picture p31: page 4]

Test Points T i t l e | Acme_CP U 3 0 N G o u l d S t s u i te 4 0 0 0 S her i d a n WY 8

Size: A | N umber: | Rev i s i o n :

/ / T ime: : : 5 PM | | Sheet o f

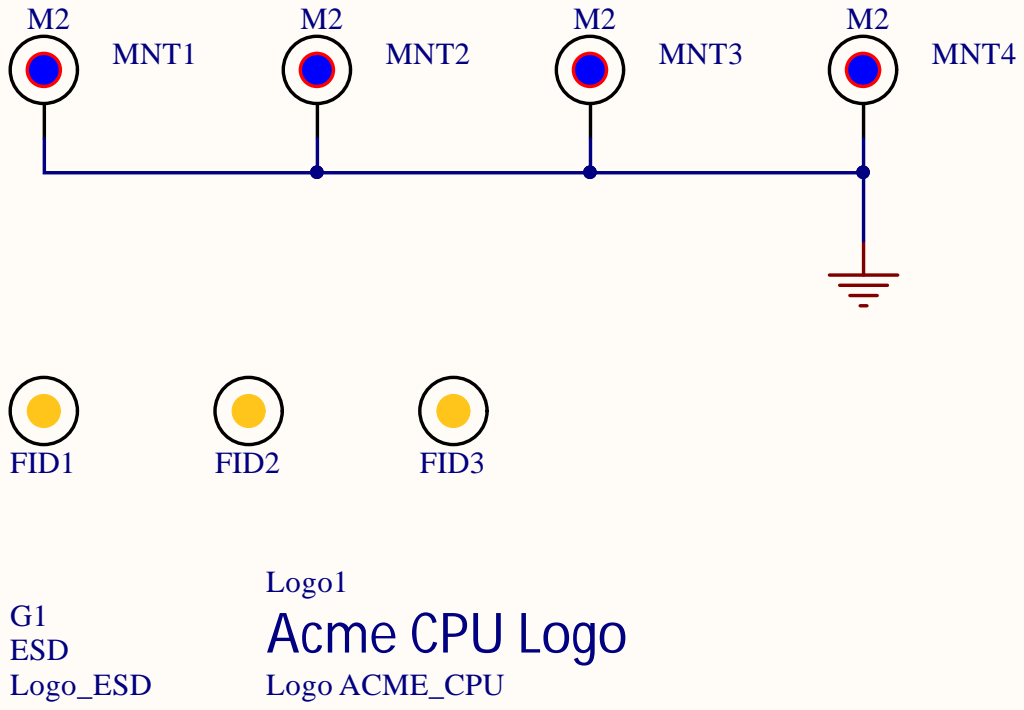
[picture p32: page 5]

Auxiliary Components Title | Acme_CPU 30 N Gould St suite 4000

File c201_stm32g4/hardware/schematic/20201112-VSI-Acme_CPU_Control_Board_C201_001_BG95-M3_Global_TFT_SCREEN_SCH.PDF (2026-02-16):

Motor Driver Block Diagra

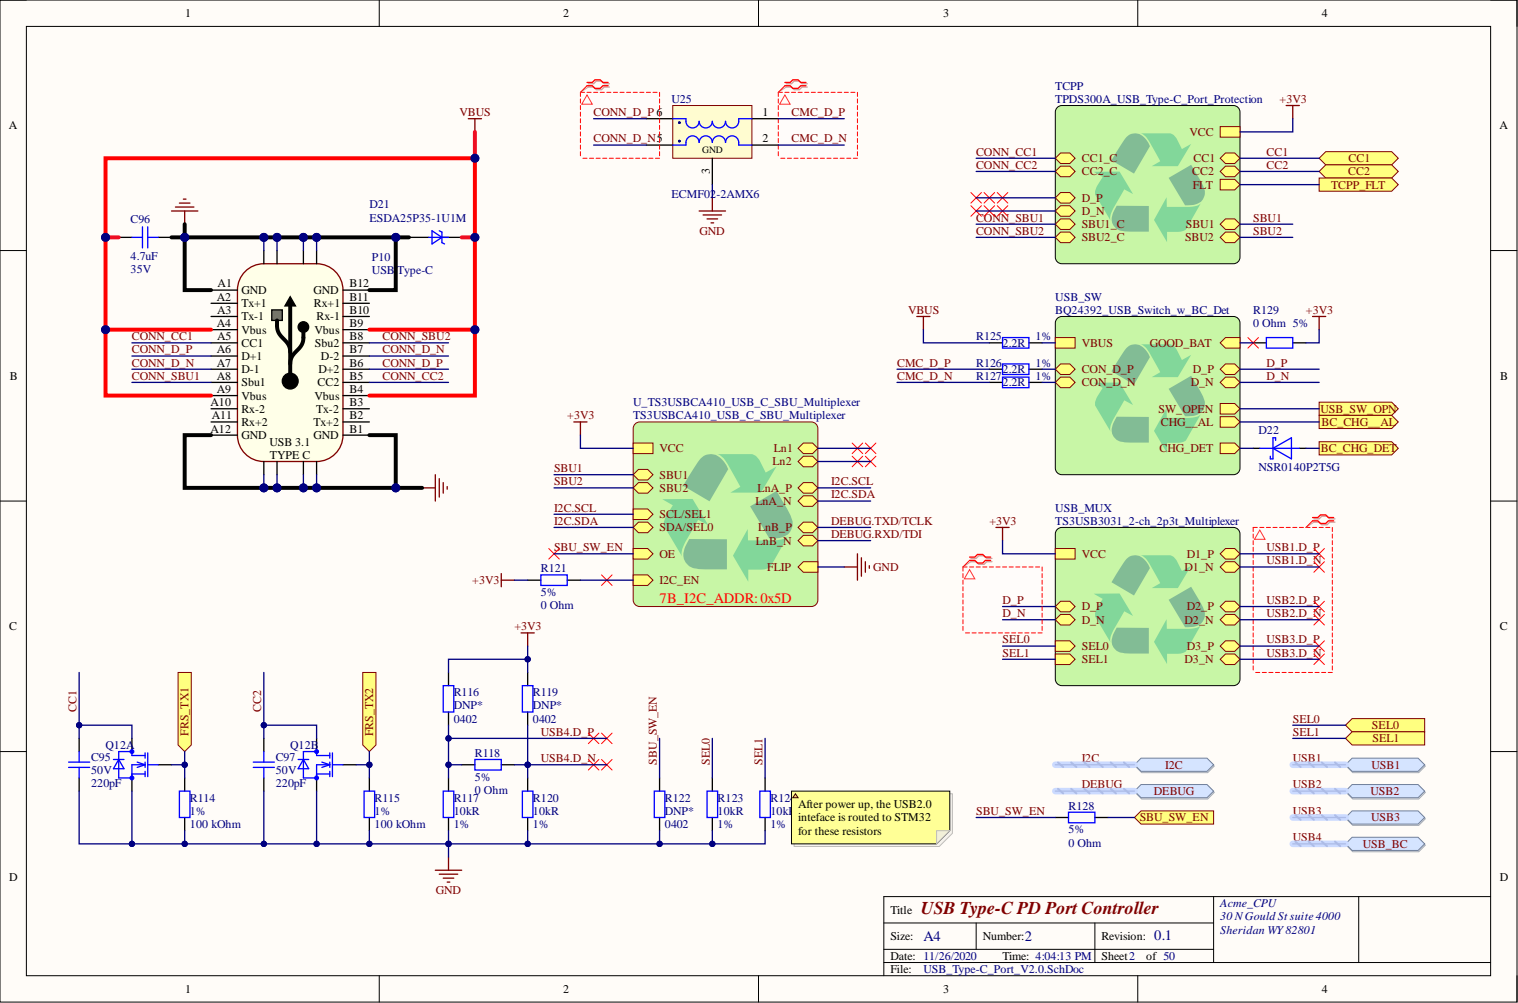
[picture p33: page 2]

USB Type-C PD Port Controller
Title

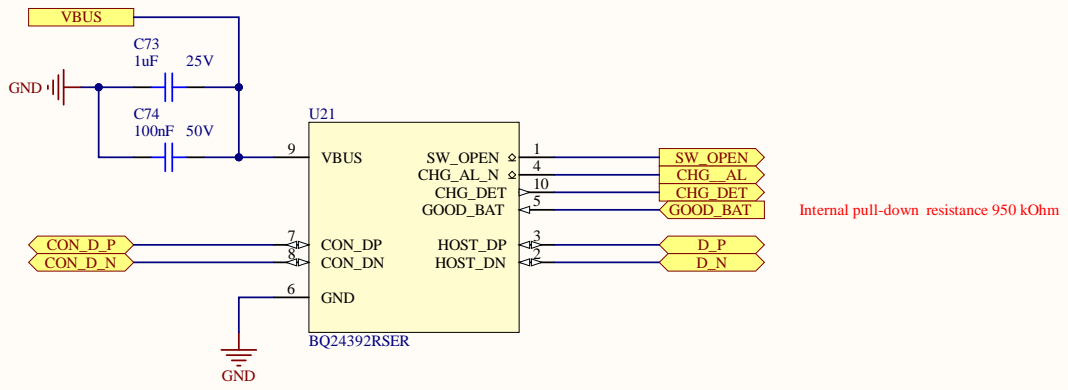
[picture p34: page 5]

VBAT VSYS

QON pulled up to

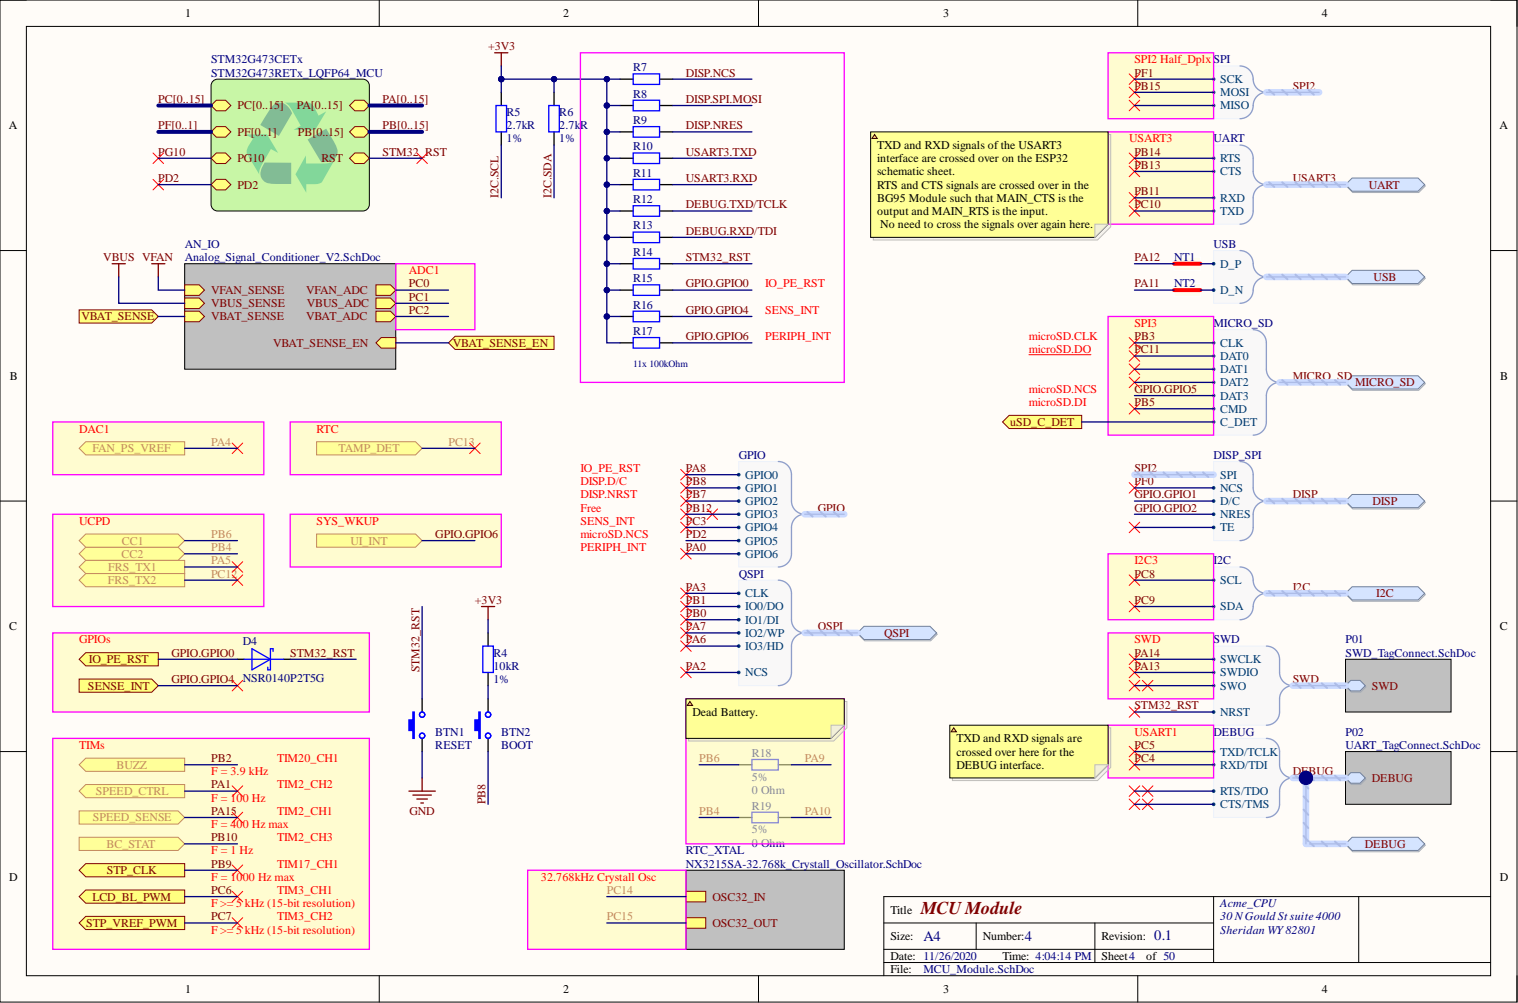
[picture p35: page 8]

microSD.NCS microSD.DI microSD.CLK microSD.DO

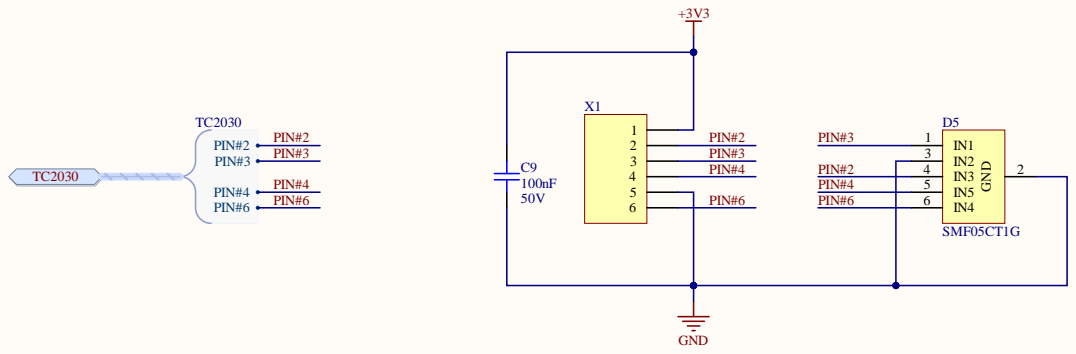
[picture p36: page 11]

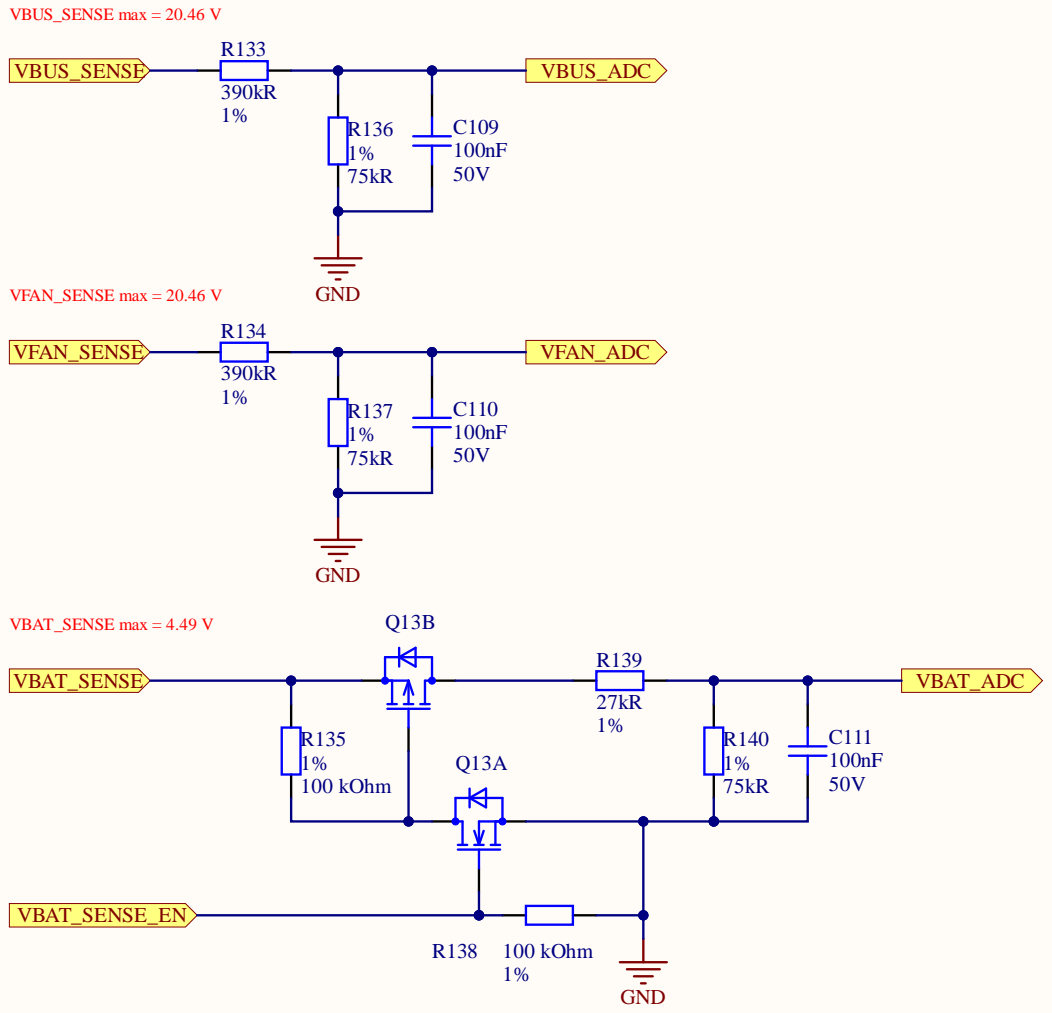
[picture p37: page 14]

1 2 3 4 5 | SCL


FREQ 9

R163 | | COMP 7


STBY/RESET
Rstby_pd = 36 kOhm
EN/FAULT
EN pull-down current 10.5 uA

STSPIN220 Stepper Motor Driver.SchDoc





QON pin of BC Controller is pulled up
to VQON through 200 kΩ. No PD here!

MP1
MP2


Each LED output can be off, on (no PWM control), set at its Individual PWM controller value or at both Individual and
Group PWM controller values. The LED output driver is programmed to be either open-drain with a 25 mA current sink
capability at 5 V or totem pole with a 25 mA sink, 10 mA source capability at 5 V. The PCA9632 operates with a supply
voltage range of 2.3 V to 5.5 V and the outputs are 5.5 V tolerant.


TXD and RXD signals of the UART1
and UART2 interfaces of the ESP32
module are crossed over here so that
if ESP32 Module is not installed and
the STM32 MCU is connected to the
BG95 Module through the resistor
array, the TXD and RXD signals of
the STM32 would meet respective
RXD and TXD signals of the BG95
Broadband Modem.

RTS and CTS signals are crossed over
in the BG95 Module so no need to
cross them over again here.

TXD and RXD signals of the
UART2 interface of the ESP32
module are crossed over here to
meet respective signals of the
BG95 Broadband Modem.

TXD and RXD and RTS and CTS signals
of the UART0 interface of the ESP32
module are crossed over here to meet
respective signals of the CP2102N
USB-UART bridge.


1 5
3 8
3 9

LED's current
Green - 2 mA or less;
Red & Blue - approx. 3-5 mA.

Forward Voltage @ desired current:
Red - 1.8 V;
Green & Blue - approx. 2.8 V.

Remote USB wakeup interrupt input.

SUSP_B is driven low while the device is in USB suspend state.
SUSP is driven high while the device in USB suspend state.

CP2102 USB-to-UART Bridge
Title


Not Fitted in BG95-M3_Global Variant VSYS

Not Fitted in BG95-M1_US Variant

Pulled up by default

Do not pull PWRKEY
down to GND permanently.

UART

MCUs for these resistors

50 Ohm matching
If unused, keep this pin open.


7 4 | 9 0
7 9 | 9 1
8 0 | 1 0 0
8 1 | 1 0 1
8 2 | 1 0 2




4 | | Vr e f = 580. . .610 mV (595 mV typ. | )
G N D FB

vers i o n o f t he I C



1 5
1 4
1 3
1 2

1 0

uSD Card Connection Port *


CTRL pin internal pull-down resistor 300 kOhm

2 2
3 3
4 4
5 5
6 6

GND

LED_K | | LED_K

3 3
4 4
5 5
6 6
7 7


QSPI.NCS QSPI.CLK


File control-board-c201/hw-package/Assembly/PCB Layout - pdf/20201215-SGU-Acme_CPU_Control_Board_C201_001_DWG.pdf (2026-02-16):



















View from Front side (Scale 2:1)


View from Back side (Scale 2:1)


View from Top side (Scale 2:1)

Ground&PowerPlanes_5 Ground&PowerPlanes_4 Ground&PowerPlanes_3 Ground&PowerPlanes_2 Ground&PowerPlanes_1


View from Bottom side (Scale 2:1)


Dimensions from Top side (Scale: 2:1)


Fiducials from Top side (Scale: 2:1)

View from Front side (Scale 2:1)


View from Back side (Scale 2:1)

View from Top side (Scale 2:1)

Ground&PowerPlanes_5 Ground&PowerPlanes_4 Ground&PowerPlanes_3 Ground&PowerPlanes_2 Ground&PowerPlanes_1

View from Bottom side (Scale 2:1)

Dimensions from Top side (Scale: 2:1)

Fiducials from Top side (Scale: 2:1)

View from Front side (Scale 2:1)

View from Back side (Scale 2:1)

View from Top side (Scale 2:1)

Ground&PowerPlanes_5 Ground&PowerPlanes_4 Ground&PowerPlanes_3 Ground&PowerPlanes_2 Ground&PowerPlanes_1

View from Bottom side (Scale 2:1)

Dimensions from Top side (Scale: 2:1)

Fiducials from Top side (Scale: 2:1)

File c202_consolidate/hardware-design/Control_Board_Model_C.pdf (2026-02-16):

AA

BB







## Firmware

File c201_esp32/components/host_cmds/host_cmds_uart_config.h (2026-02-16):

/*
 * Copyright (c) 2022 Acme CPU
 *
 * host_cmds_uart_config.h
 * Created on: 20-Sep-2022
 *     Author: Rohan Dey (rohan@acmecpu.com)
 */

#ifndef COMPONENTS_HOST_CMDS_HOST_CMDS_UART_CONFIG_H_
#define COMPONENTS_HOST_CMDS_HOST_CMDS_UART_CONFIG_H_

#ifdef __cplusplus
extern "C" {
#endif


/*
 * #define CONFIG_HOST_IF_UART_NUMBER 2
#define CONFIG_HW_FLOWCTRL_CTS_RTS 1
#define CONFIG_HOST_IF_UART_RX_PIN 16
#define CONFIG_HOST_IF_UART_TX_PIN 17
#define CONFIG_HOST_IF_UART_RTS_PIN 33
#define CONFIG_HOST_IF_UART_CTS_PIN 35
 * */

#if CONFIG_BOARD_C201
#define UART_NUM		2

#define HW_FLOWCTRL_DISABLE 0
#define HW_FLOWCTRL_RTS 0
#define HW_FLOWCTRL_CTS 0
#define HW_FLOWCTRL_CTS_RTS 1

#define TXD_PIN 		17
#define RXD_PIN 		16
#define RTS_PIN 		33
#define CTS_PIN 		35

#elif CONFIG_BOARD_C204

#define UART_NUM		1

#define HW_FLOWCTRL_DISABLE 0
#define HW_FLOWCTRL_RTS 0
#define HW_FLOWCTRL_CTS 0
#define HW_FLOWCTRL_CTS_RTS 1

#define TXD_PIN 		26
#define RXD_PIN 		25
#define RTS_PIN 		14
#define CTS_PIN 		27

#elif CONFIG_BOARD_E206

#define UART_NUM		1

#define HW_FLOWCTRL_DISABLE 0
#define HW_FLOWCTRL_RTS 0
#define HW_FLOWCTRL_CTS 0
#define HW_FLOWCTRL_CTS_RTS 1

#define TXD_PIN 		26
#define RXD_PIN 		25
#define RTS_PIN 		14
#define CTS_PIN 		27

#elif CONFIG_BOARD_H205C

#define UART_NUM		1

#define HW_FLOWCTRL_DISABLE 0
#define HW_FLOWCTRL_RTS 0
#define HW_FLOWCTRL_CTS 0
#define HW_FLOWCTRL_CTS_RTS 1

#define TXD_PIN 		18
#define RXD_PIN 		17
#define RTS_PIN 		20
#define CTS_PIN 		19

#endif

#define RX_BUF_SIZE		4096
#define RETRY_COUNT		10

#ifdef __cplusplus
}
#endif

#endif /* COMPONENTS_HOST_CMDS_HOST_CMDS_UART_CONFIG_H_ */

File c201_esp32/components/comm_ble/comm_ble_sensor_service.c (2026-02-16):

/*
 * Copyright (c) 2022 Acme CPU
 *
 * comm_ble_sensor_service.c
 * Created on: 10-Aug-2022
 *     Author: Rohan Dey (rohan@acmecpu.com)
 */


#include "freertos/FreeRTOS.h"
#include "freertos/task.h"
#include "freertos/event_groups.h"
#include "freertos/semphr.h"
#include "esp_system.h"
#include "esp_log.h"
#include "nvs_flash.h"
#include "esp_bt.h"

#include "esp_gap_ble_api.h"
#include "esp_gatts_api.h"
#include "esp_bt_main.h"
#include "esp_gatt_common_api.h"
#include <string.h>
#include <stdlib.h>

#include "host_cmds.h"
#include "host_cmds_callback.h"
#include "comm_ble_common.h"
#include "comm_ble_blower_device_profile.h"
#include "comm_ble_sensor_service.h"
#include "app_events.h"
#include "c20x_m2m_cmds.h"

//#include "m2m_frame.h"
#include "lib_m2m_frame.h"
#define TAG	"comm_ble_sensor_svc"

#define SVC_INST_ID             	0

/* App event related data */
static struct app_events_callback m_evntcb_toupdt_coproc;
static struct app_events_callback m_evntcb_updting_coproc;
static struct app_events_callback m_evntcb_updted_coproc;
static void app_event_handler(struct app_events_callback *cb, APP_EVENT_TYPE event);


typedef enum {
	TASK_SENSOR_GET=0,
	TASK_SENSOR_GETALL,
	TASK_NB
} SENSOR_TASK_IDX;
#define NUM_NOTIFY_TASKS		(TASK_NB)

struct sensor_task_control {
	TaskHandle_t ntf_task;
	bool stay_alive;
};

static struct sensor_task_control m_sen_task_ctrl[NUM_NOTIFY_TASKS] = {
	[TASK_SENSOR_GET] = {.ntf_task = NULL, .stay_alive = false},
};
static esp_gatt_if_t m_gatts_if;
static uint16_t m_conn_id;

static void task_sensor_get_notify( void * pvParameters );
static void task_sensor_getall_notify( void * pvParameters );

/* Sensor Service Attribute Indexes */
enum {
    SEN_IDX_SVC,

    SEN_IDX_LIST_CHAR,
    SEN_IDX_LIST_VAL,

    SEN_IDX_GET_CHAR,
    SEN_IDX_GET_VAL,
	SEN_IDX_GET_NTF_CFG,

	SEN_IDX_GETALL_CHAR,
    SEN_IDX_GETALL_VAL,
	SEN_IDX_GETALL_NTF_CFG,

	SEN_IDX_GETALL_INTV_CHAR,
    SEN_IDX_GETALL_INTV_VAL,

	SEN_IDX_NB,
};

/* Array of handles to each element */
static uint16_t handle_table_sensor[SEN_IDX_NB];

/* Sensor Service UUID */
static const uint16_t m_sensor_svc 				= 0x8050;
static const uint16_t m_sensor_list_uuid 		= 0x8051;
static const uint16_t m_sensor_get_uuid 		= 0x8052;
static uint8_t m_sensor_get_ccc[2]				= { 0x00, 0x00}; /* keep notifications disabled by default */
static const uint16_t m_sensor_getall_uuid 		= 0x8053;
static const uint16_t m_getall_intv_uuid 		= 0x8054;
static uint8_t m_sensor_getall_ccc[2]			= { 0x00, 0x00}; /* keep notifications disabled by default */
static uint32_t m_getall_interval				= 50;	/* interval in ms */

static uint8_t m_sensor_list[SENSOR_LIST_MAX_LEN]				= {0x00};
static uint8_t m_sensor_get_value[SENSOR_GET_VAL_MAX_LEN]		= {0x00};
static uint8_t m_sensor_getall_value[SENSOR_GETALL_VAL_MAX_LEN]	= {0x00};

static uint32_t m_sensor_list_len = 0;
static uint32_t m_sensor_get_len = 0;
static uint32_t m_sensor_getall_len = 0;


/* Sensor Service Database Description */
static const esp_gatts_attr_db_t gatt_db_sensor_svc[SEN_IDX_NB] =
{
		// Sensor Service Declaration
		[SEN_IDX_SVC] =
		{ { ESP_GATT_AUTO_RSP }, { ESP_UUID_LEN_16, (uint8_t*) &primary_service_uuid, ESP_GATT_PERM_READ,
		sizeof(uint16_t), sizeof(m_sensor_svc), (uint8_t*) &m_sensor_svc } },

		// Sensor List Characteristic Declaration
		[SEN_IDX_LIST_CHAR] =
		{ { ESP_GATT_RSP_BY_APP }, { ESP_UUID_LEN_16, (uint8_t*) &character_declaration_uuid, ESP_GATT_PERM_READ,
		CHAR_DECLARATION_SIZE, CHAR_DECLARATION_SIZE, (uint8_t*) &char_prop_read } },

		// Sensor List Characteristic Value
		[SEN_IDX_LIST_VAL] =
		{ { ESP_GATT_RSP_BY_APP }, { ESP_UUID_LEN_16, (uint8_t*) &m_sensor_list_uuid, ESP_GATT_PERM_READ_ENCRYPTED,
		GATTS_CHAR_VAL_LEN_MAX, sizeof(m_sensor_list), (uint8_t*) m_sensor_list } },

		// Sensor Get Characteristic Declaration
		[SEN_IDX_GET_CHAR] =
		{ { ESP_GATT_RSP_BY_APP }, { ESP_UUID_LEN_16, (uint8_t*) &character_declaration_uuid, ESP_GATT_PERM_READ | ESP_GATT_PERM_WRITE,
		CHAR_DECLARATION_SIZE, CHAR_DECLARATION_SIZE, (uint8_t*) &char_prop_read_write_notify } },

		// Sensor Get Characteristic Value
		[SEN_IDX_GET_VAL] =
		{ { ESP_GATT_RSP_BY_APP }, { ESP_UUID_LEN_16, (uint8_t*) &m_sensor_get_uuid, ESP_GATT_PERM_READ_ENCRYPTED | ESP_GATT_PERM_WRITE_ENCRYPTED,
		GATTS_CHAR_VAL_LEN_MAX, sizeof(m_sensor_get_value), (uint8_t*) m_sensor_get_value } },

		// Sensor Get Characteristic - Client Characteristic Configuration Descriptor
		[SEN_IDX_GET_NTF_CFG] =
		{ { ESP_GATT_AUTO_RSP }, { ESP_UUID_LEN_16, (uint8_t*) &character_client_config_uuid, ESP_GATT_PERM_READ_ENCRYPTED | ESP_GATT_PERM_WRITE_ENCRYPTED,
		sizeof(uint16_t), sizeof(m_sensor_get_ccc), (uint8_t*) m_sensor_get_ccc } },

		// Sensor Get All Characteristic Declaration
		[SEN_IDX_GETALL_CHAR] =
		{ { ESP_GATT_RSP_BY_APP }, { ESP_UUID_LEN_16, (uint8_t*) &character_declaration_uuid, ESP_GATT_PERM_READ|ESP_GATT_PERM_WRITE,
		CHAR_DECLARATION_SIZE, CHAR_DECLARATION_SIZE, (uint8_t*) &char_prop_read_write_notify } },

		// Sensor Get All Characteristic Value
		[SEN_IDX_GETALL_VAL] =
		{ { ESP_GATT_RSP_BY_APP }, { ESP_UUID_LEN_16, (uint8_t*) &m_sensor_getall_uuid, ESP_GATT_PERM_READ_ENCRYPTED | ESP_GATT_PERM_WRITE_ENCRYPTED,
		GATTS_CHAR_VAL_LEN_MAX, sizeof(m_sensor_getall_value), (uint8_t*) m_sensor_getall_value } },

		// Sensor Get All Characteristic - Client Characteristic Configuration Descriptor
		[SEN_IDX_GETALL_NTF_CFG] =
		{ { ESP_GATT_AUTO_RSP }, { ESP_UUID_LEN_16, (uint8_t*) &character_client_config_uuid, ESP_GATT_PERM_READ_ENCRYPTED | ESP_GATT_PERM_WRITE_ENCRYPTED,
		sizeof(uint16_t), sizeof(m_sensor_getall_ccc), (uint8_t*) m_sensor_getall_ccc } },

		// Sensor Getall Interval Characteristic Declaration
		[SEN_IDX_GETALL_INTV_CHAR] =
		{ { ESP_GATT_RSP_BY_APP }, { ESP_UUID_LEN_16, (uint8_t*) &character_declaration_uuid, ESP_GATT_PERM_READ|ESP_GATT_PERM_WRITE,
		CHAR_DECLARATION_SIZE, CHAR_DECLARATION_SIZE, (uint8_t*) &char_prop_read_write_notify } },

		// Sensor Get All Characteristic Value
		[SEN_IDX_GETALL_INTV_VAL] =
		{ { ESP_GATT_RSP_BY_APP }, { ESP_UUID_LEN_16, (uint8_t*) &m_getall_intv_uuid, ESP_GATT_PERM_READ_ENCRYPTED | ESP_GATT_PERM_WRITE_ENCRYPTED,
		GATTS_CHAR_VAL_LEN_MAX, sizeof(m_getall_interval), (uint8_t*) &m_getall_interval } },
};

/* Callback data and functions */
typedef enum {
	CB_LIST=0,
	CB_GET,
	CB_GET_ALL,
	CB_NB
} READ_CB;
#define NUM_READ_CB		(CB_NB)

static struct host_cmd_callback cb_sensor_get_list;			/* sensor get list callback object */
static struct host_cmd_callback cb_sensor_get_value;		/* sensor get value callback object */
static struct host_cmd_callback cb_sensor_getall_value;		/* sensor getall value callback object */

struct cmd_read_cb {
	bool data_available;
	SemaphoreHandle_t cmd_mutex;
};
static struct cmd_read_cb m_cb_data[NUM_READ_CB];

void cb_handler_sensor_list(struct host_cmd_callback *cb, uint32_t cmd, void *frame) {
	ESP_LOGI(TAG, "cb_handler_sensor_list");

	struct m2m_frame_t *fr = (struct m2m_frame_t *) frame;

	if (fr->type != UART_M2M_FRAME_SINGLE_RESP) {
		ESP_LOGE(TAG, "Invalid Frame type");
		return;
	}

	if (fr->payload_len <= 0) {
		ESP_LOGE(TAG, "Invalid payload length");
		return;
	}

	/* copy the payload */
	char pl_excl[10] = {0x00};
	uint8_t pl_excl_len = sprintf(pl_excl, "%d%s", C20X_M2M_CMD_ID_SENSOR_LIST, M2M_CMD_PAYLOAD_DELIM);

	m_sensor_list_len = fr->payload_len - pl_excl_len;
	memcpy(m_sensor_list, fr->payload + pl_excl_len, fr->payload_len-1 /* exclude the terminating character */);

	/* set data available variable to true */
	if (m_cb_data[CB_LIST].cmd_mutex != NULL) {
		if (xSemaphoreTake(m_cb_data[CB_LIST].cmd_mutex, (TickType_t) 10/portTICK_PERIOD_MS ) == pdTRUE) {
			m_cb_data[CB_LIST].data_available = true;
			xSemaphoreGive(m_cb_data[CB_LIST].cmd_mutex);
		}
	}
}

void cb_handler_sensor_get(struct host_cmd_callback *cb, uint32_t cmd, void *frame) {
	ESP_LOGI(TAG, "cb_handler_sensor_get");

	struct m2m_frame_t *fr = (struct m2m_frame_t *) frame;

	if (fr->type != UART_M2M_FRAME_SINGLE_RESP) {
		ESP_LOGE(TAG, "Invalid Frame type");
		return;
	}

	if (fr->payload_len <= 0) {
		ESP_LOGE(TAG, "Invalid payload length");
		return;
	}

	/* copy the payload */
	char pl_excl[10] = {0x00};
	uint8_t pl_excl_len = sprintf(pl_excl, "%d%s", C20X_M2M_CMD_ID_SENSOR_GET, M2M_CMD_PAYLOAD_DELIM);

	m_sensor_get_len = fr->payload_len - pl_excl_len;
	memcpy(m_sensor_get_value, fr->payload + pl_excl_len, fr->payload_len-1 /* exclude the terminating character */);

	/* set data available variable to true */
	if (m_cb_data[CB_GET].cmd_mutex != NULL) {
		if (xSemaphoreTake(m_cb_data[CB_GET].cmd_mutex, (TickType_t) 10/portTICK_PERIOD_MS ) == pdTRUE) {
			m_cb_data[CB_GET].data_available = true;
			xSemaphoreGive(m_cb_data[CB_GET].cmd_mutex);
		}
	}
}

void cb_handler_sensor_getall(struct host_cmd_callback *cb, uint32_t cmd, void *frame) {
	ESP_LOGI(TAG, "cb_handler_sensor_getall");

	struct m2m_frame_t *fr = (struct m2m_frame_t *) frame;

	if (fr->type != UART_M2M_FRAME_SINGLE_RESP) {
		ESP_LOGE(TAG, "Invalid Frame type");
		return;
	}

	if (fr->payload_len <= 0) {
		ESP_LOGE(TAG, "Invalid payload length");
		return;
	}

	/* copy the payload */
	char pl_excl[10] = {0x00};
	uint8_t pl_excl_len = sprintf(pl_excl, "%d%s", C20X_M2M_CMD_ID_SENSOR_GET, M2M_CMD_PAYLOAD_DELIM);

	m_sensor_getall_len = fr->payload_len - pl_excl_len;
	memcpy(m_sensor_getall_value, fr->payload + pl_excl_len, fr->payload_len-1 /* exclude the terminating character */);

	/* set data available variable to true */
	if (m_cb_data[CB_GET_ALL].cmd_mutex != NULL) {
		if (xSemaphoreTake(m_cb_data[CB_GET_ALL].cmd_mutex, (TickType_t) 10/portTICK_PERIOD_MS ) == pdTRUE) {
			m_cb_data[CB_GET_ALL].data_available = true;
			xSemaphoreGive(m_cb_data[CB_GET_ALL].cmd_mutex);
		}
	}
}

static void cmd_read_register_callback() {
	m_cb_data[CB_LIST].cmd_mutex = xSemaphoreCreateMutex();
	host_cmds_add_callback(&cb_sensor_get_list, cb_handler_sensor_list, C20X_M2M_CMD_ID_SENSOR_LIST);

	m_cb_data[CB_GET].cmd_mutex = xSemaphoreCreateMutex();
	host_cmds_add_callback(&cb_sensor_get_value, cb_handler_sensor_get, C20X_M2M_CMD_ID_SENSOR_GET);

	m_cb_data[CB_GET_ALL].cmd_mutex = xSemaphoreCreateMutex();
	host_cmds_add_callback(&cb_sensor_getall_value, cb_handler_sensor_getall, C20X_M2M_CMD_ID_SENSOR_GETALL);
}

static uint8_t find_char_and_desr_index(uint16_t handle, uint16_t *table, int num_elem) {
	uint8_t error = 0xff;

	for (int i = 0; i < num_elem; i++) {
		if (handle == table[i]) {
			return i;
		}
	}
	return error;
}

static int update_data_availability(SemaphoreHandle_t mutex, bool *pvar, bool val) {
	if (mutex != NULL) {
		if (xSemaphoreTake(mutex, (TickType_t) 10/portTICK_PERIOD_MS ) == pdTRUE) {
			*pvar = val;
			xSemaphoreGive(mutex);
			return 0;
		} else {
			return -1;
		}
	}
	return -1;
}

#define DATA_AVAILABLE_LOOP_DELAY_SENSOR	(1 / portTICK_PERIOD_MS)
static int wait_until_timeout(bool *pvar) {
//	bool wait_timeout = false;
	uint32_t delay = 0;
	while (!(*pvar)) {
		vTaskDelay(DATA_AVAILABLE_LOOP_DELAY_SENSOR);
		delay += DATA_AVAILABLE_LOOP_DELAY_SENSOR;
		if (delay > DATA_AVAILABLE_TIMEOUT) {
//			wait_timeout = true;
			return -1;
		}
	}
	return 0;
}

static int send_ble_response(esp_gatt_if_t gatts_if, esp_ble_gatts_cb_param_t *param, uint32_t len, void *data) {
	esp_gatt_rsp_t rsp;
    memset(&rsp, 0, sizeof(esp_gatt_rsp_t));
    rsp.attr_value.handle = param->read.handle;
    rsp.attr_value.len = len;
    memcpy(rsp.attr_value.value, data, len);
    return esp_ble_gatts_send_response(gatts_if, param->read.conn_id, param->read.trans_id, ESP_GATT_OK, &rsp);
}
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

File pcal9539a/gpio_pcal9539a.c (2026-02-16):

/*
 * Copyright (c) 2021 Acme CPU
 * Copyright (c) 2015 Intel Corporation.
 * Copyright (c) 2020 Norbit ODM AS
 *
 * SPDX-License-Identifier: Apache-2.0
 */

#define DT_DRV_COMPAT nxp_pcal9539a

#define ACPU_ENABLE		0
/**
 * @file Driver for PCAL9539A I2C-based GPIO driver.
 */

#include <errno.h>

#include <zephyr/kernel.h>
#include <zephyr/device.h>
#include <zephyr/init.h>
#include <zephyr/sys/byteorder.h>
#include <zephyr/sys/util.h>
#include <zephyr/drivers/gpio.h>
#include <zephyr/drivers/i2c.h>

#include "gpio_utils.h"

#define LOG_LEVEL CONFIG_GPIO_LOG_LEVEL
#include <zephyr/logging/log.h>
LOG_MODULE_REGISTER(gpio_pcal9539a);

/* Register definitions */
#define REG_INPUT_PORT0			0x00
#define REG_INPUT_PORT1			0x01
#define REG_OUTPUT_PORT0		0x02
#define REG_OUTPUT_PORT1		0x03
#define REG_POL_INV_PORT0		0x04
#define REG_POL_INV_PORT1		0x05
#define REG_CONF_PORT0			0x06
#define REG_CONG_PORT1			0x07
#define REG_OUT_DRV_STRENGTH_PORT0_L	0x40
#define REG_OUT_DRV_STRENGTH_PORT0_H	0x41
#define REG_OUT_DRV_STRENGTH_PORT1_L	0x42
#define REG_OUT_DRV_STRENGTH_PORT1_H	0x43
#define REG_INPUT_LATCH_PORT0		0x44
#define REG_INPUT_LATCH_PORT1		0x45
#define REG_PUD_EN_PORT0		0x46
#define REG_PUD_EN_PORT1		0x47
#define REG_PUD_SEL_PORT0		0x48
#define REG_PUD_SEL_PORT1		0x49
#define REG_INT_MASK_PORT0		0x4A
#define REG_INT_MASK_PORT1		0x4B
#define REG_INT_STATUS_PORT0		0x4C
#define REG_INT_STATUS_PORT1		0x4D
#define REG_OUTPUT_PORT_CONF		0x4F

/* Driver flags */
#define PCA_HAS_PUD			BIT(0)
#define PCA_HAS_INTERRUPT		BIT(1)
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
